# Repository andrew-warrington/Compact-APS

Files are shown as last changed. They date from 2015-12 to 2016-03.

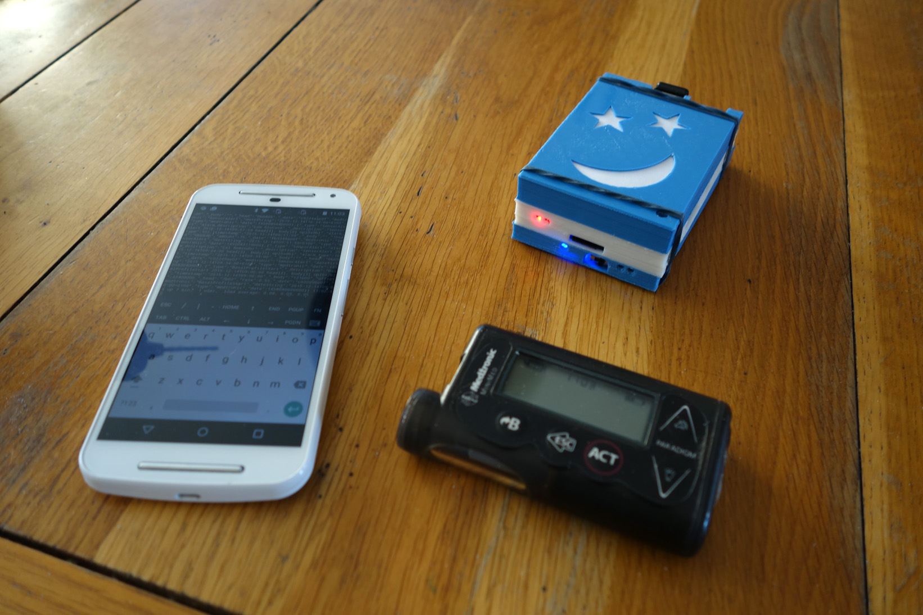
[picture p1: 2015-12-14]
Images/03 v1 assembled (except bolts) - angle 3.jpg

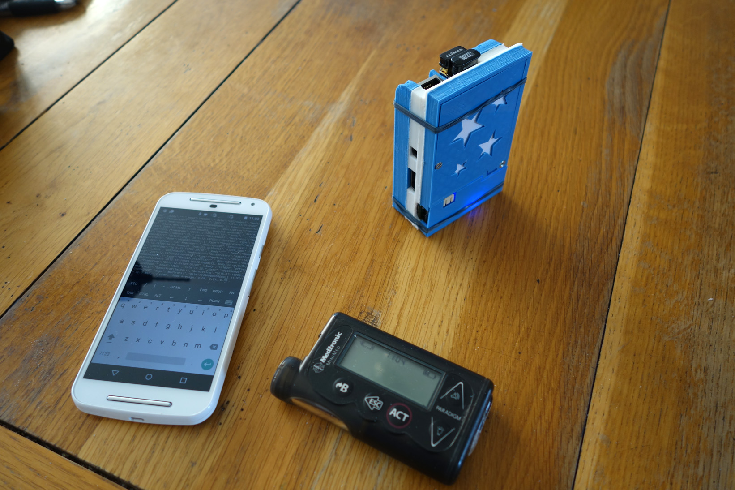
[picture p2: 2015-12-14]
Images/02 v1 assembled (except bolts) - angle 2.jpg

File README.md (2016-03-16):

# Compact-APS

This repository contains a compact hardware configuration for a DIY APS system based on the OpenAPS toolset. The goal of this build is to put everything needed for an OpenAPS-based implementation in a single box, including the battery. Pictures are available in the Images folder of this repository. The custom case files are in the Case folder.

- V1 is designed for a Raspberry Pi / Carelink config.
- V3.2 is designed for a Edison / TI USB CC1111 dongle config (mmeowlink)

If you are just starting out, I recommend the Edison v3.2 due to smaller size and longer battery life.

## V1 (Raspberry Pi) info

- Battery life 5 hours, with 5 hours recharge time while running.
- 10 cm long
- 6.2 cm wide
- 3 cm high

The device supports reading from Medtronic pumps & CGM, as well as Dexcom (I think! I don't have a Dexcom to test with...). It includes Wifi and BLE hardware support as well, via USB dongles.

The main tactic for reducing the footprint was to reverse one of the USB ports on the RPi2, so that the Carelink USB dongle is positioned over the RPi and not protrude outwards.

Due to the inclusion of an Adafruit PowerBoost charger, the device charges like a mobile phone - no need to shut it down and swap around USB cables. Just plug it in and it will charge while running. An attempt was made to include wireless charging as well - this was not immediately successful so will be added in a later version if possible.

The "Moon and stars" face on the top cover helps to remember how to place the device to have the optimum angle for communicating with the Carelink USB. If the face is looking at you, then it is likely in a good position for communication. :)

v1 design includes the following components:

- 1 Raspberry Pi 2 + SD card with NOOB Raspian and some extra space (standard stuff)
- 1 standard dual-port PCB-mountable USB connector (dismantled and rebuilt to face backwards - this would take some time to explain and so I will describe it further at a later time)
- 1 Carelink USB dongle
- 1 Adafruit PowerBoost 1000C
- 1 Power switch for the PowerBoost 1000C
- 1 Duracell DRSI9220 Lithium Ion battery (Samsung Galaxy Note replacement battery) - 2500 mAh
- 1 mobile phone battery connector (salvaged from an inexpensive Samsung mobile phone)
- 1 Wixel (to collect data from Dexcom CGM in an Xdrip configuration. Not tested as I don't have a Dexcom...)
- 1 Asus USB-BT400 Bluetooth 4.0 dongle (for Xdrip configuration but also might be used to connect via an app one day)
- 1 Edimax EW-7811UN Nano WiFi adapter
- 1 Medtronic remote control MMT-503EU, plus A23 12-volt battery, plus 3 x 4N25 optocouplers (this was for an experiment. it worked, but it was irritating, so it will be removed in v2)
- 1 home-designed and printed 3D case (files available in this repo)
- m2.5 x 8 nuts & bolts (cut down to various lengths as needed)
- m2.5 x 30 nuts & bolts (cut down to various lengths as needed)

+ bits of wire, solder, heat-shrink, the occasional piece of electrical tape, tools, sweat, tears.

Getting started? I started here, learning to desolder components on the Raspberry Pi.
https://blog.adafruit.com/2014/11/03/diet-raspberry-pi-its-only-wafer-thin-raspberry_pi-raspberrypi/

## V3.2 (Edison) info:
- Battery life 31+ hours, with 2.5 hours recharge time while running.
- 9.6 cm long
- 6.1 cm wide
- 2.8 cm high
... with rounded edges to be easier to put in a pocket!

v3.2 design includes the following components:
- 1 Intel Edison with mini-breakout board
    - includes WiFi and BLE on board
    - the Edison USB pins 4 & 5 are shorted to force it persistently into host mode
- 1 custom USB OTG adapter, made small to save space
- 1 power switch
- 2 Duracell DRSI9220 Lithium Ion battery (Samsung Galaxy Note replacement battery), in series for 7.4V
- 1 FatShark 7.4 LiIon battery, which was disassembled to yield:
    - The balance charging circuit
    - The balance charging cable
    - The power cable
- 1 FatShark 7.4v 1000mAh wall charger
- 1 TI USB dongle CC1111EMK868-915 running the excellent subg-rfspy and managed via mmeowlink
- 1 Medtronic remote controlled via Edison GPIO (which most people would not need)

The case was further simplified over v1 to not require any screws or bolts.... also because this helps reduce size! The top snaps on and off with clips.

I don't have time to document everything for this build at the moment unfortunately, but am happy to interact, answer individual questions, and improve the documentation from there based on what questions come up. Contact me if you want help.

Best wishes, Andrew Warrington

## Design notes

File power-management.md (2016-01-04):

Notes for an eventual document on power management

Ideas sourced from here, where original contributors are mentioned:
http://babaawesam.com/2014/01/24/power-saving-tips-for-raspberry-pi/

##Underclocking the RPi2. 

tested

Adding these lines to your config.txt (assuming RPi2 has not been overclocked)
* arm_freq_min=250
* core_freq_min=100
* sdram_freq_min=150

Do not add bullets before the lines. Reboot after adding the lines.

With these lines added, the processor runs at 250 mhz when idle, and returns to 900 mhz when active. I have seen no performance decrease from this change.

You can check your processor speed with the command

`cat /sys/devices/system/cpu/cpu0/cpufreq/scaling_cur_freq`

##Powering off USB & ethernet ports between loops (or permanently!)

tested

https://github.com/codazoda/hub-ctrl.c

worst case: returns to normal after a reboot

##Powering off HDMI

not yet tested

Warning, does not return to normal after a reboot. Recommend to add the HDMI power on command to crontab @reboot.

If your system is headless (no video output) you can turn off the HDMI port with:

`sudo /opt/vc/bin/tvservice -o`

to turn it back on:

`sudo /opt/vc/bin/tvservice -p`

This command will save you around 20-30mA.

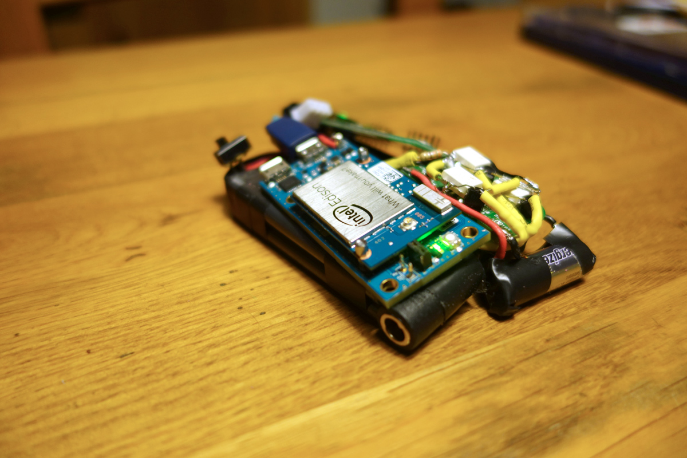
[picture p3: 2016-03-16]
Images/V3.2 interior showing at right the Medtronic remote and its batt, which most people dont need.JPG

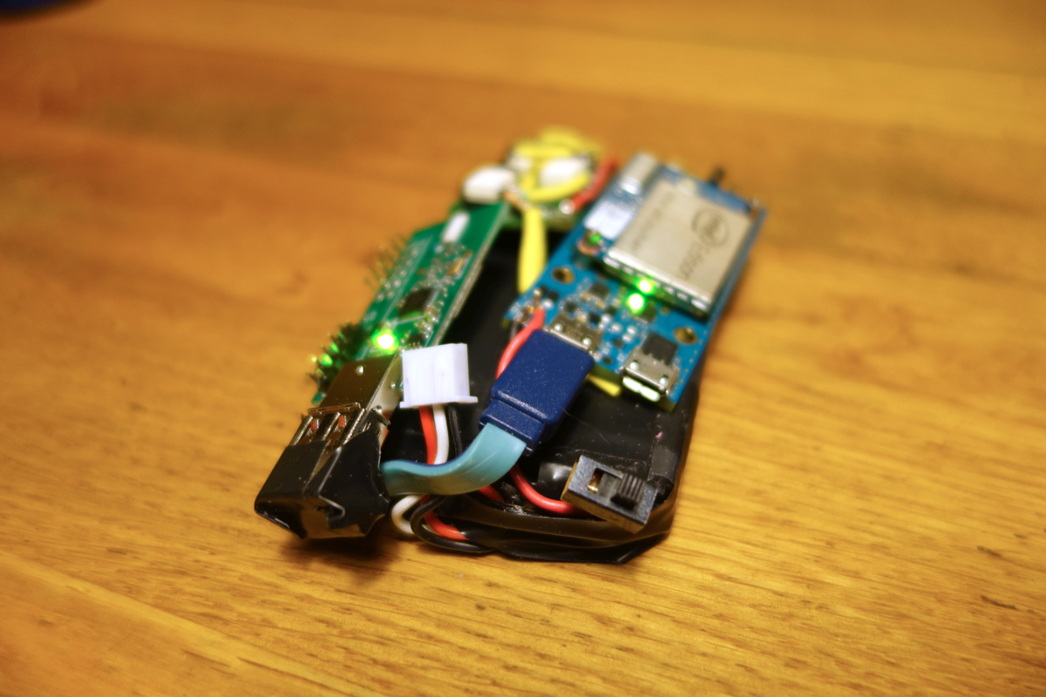
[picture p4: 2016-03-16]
Images/V3.2 interior showing custom USB connector, batt balancing cable and TI stick. Batts are underneath.JPG

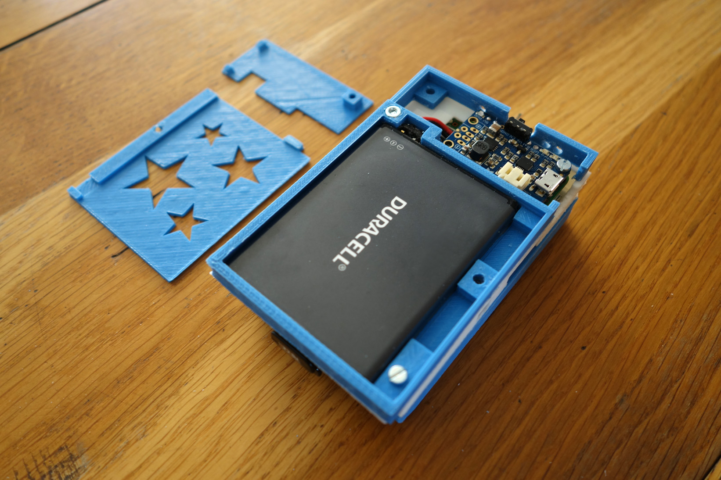
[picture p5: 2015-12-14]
Images/06 v1 underside showing the battery.jpg

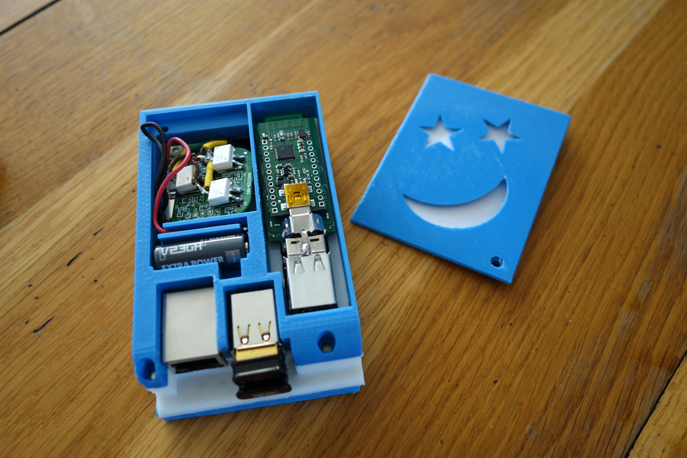
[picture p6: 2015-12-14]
Images/04 v1 under the lid.jpg

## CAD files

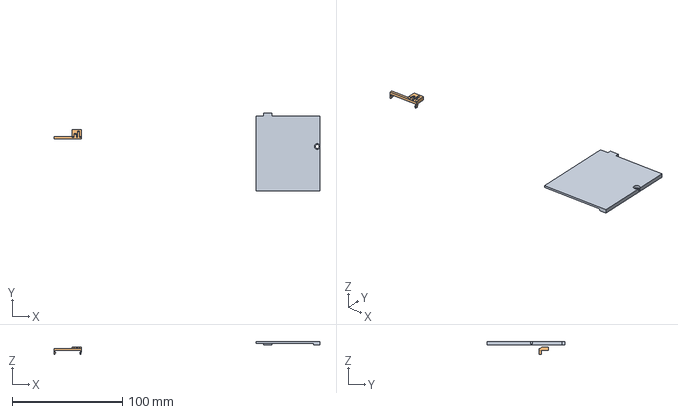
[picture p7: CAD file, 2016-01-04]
Case/FreeCAD/APS case v1.1.FCStd
241.8 x 71.0 x 11.5 mm
Main battery cover003

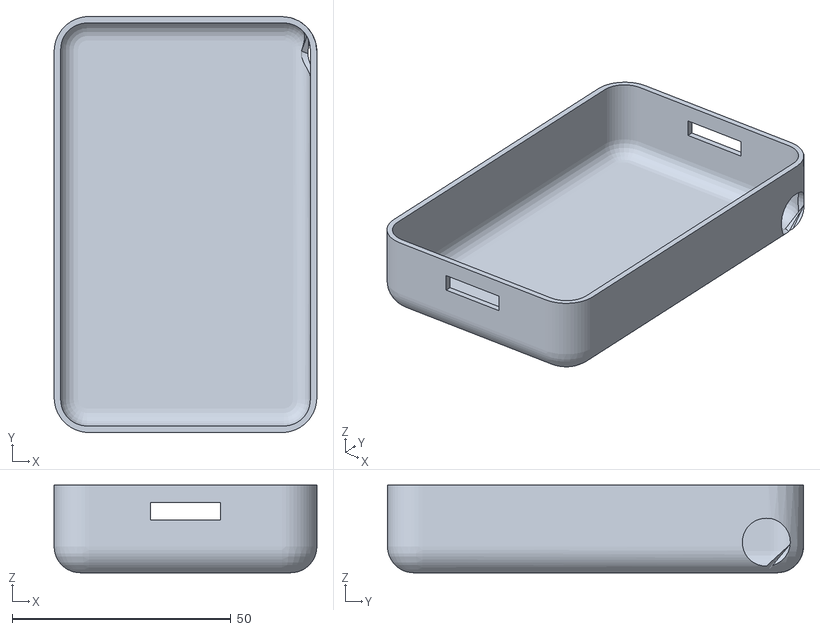
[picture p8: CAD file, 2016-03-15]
Case/STL mesh/CompactAPS v3.2 bottom final.stl
60.0 x 95.0 x 20.0

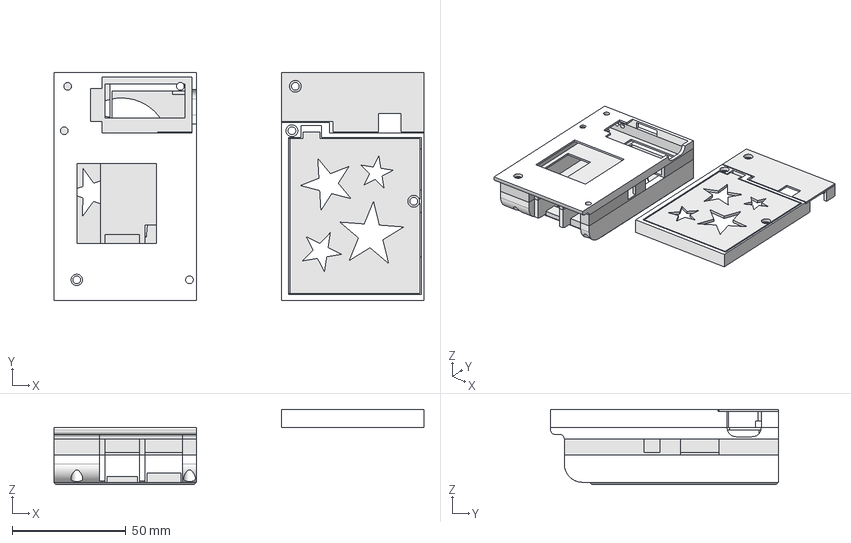
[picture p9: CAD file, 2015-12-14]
Case/FreeCAD/APS case v1.FCStd
162.5 x 100.0 x 33.0 mm
Pi case017
Pi case layer 3 009
Pi case layer 2 013
Main battery compartment022
Adafruit cover 004
Main battery cover010
Top cover 010

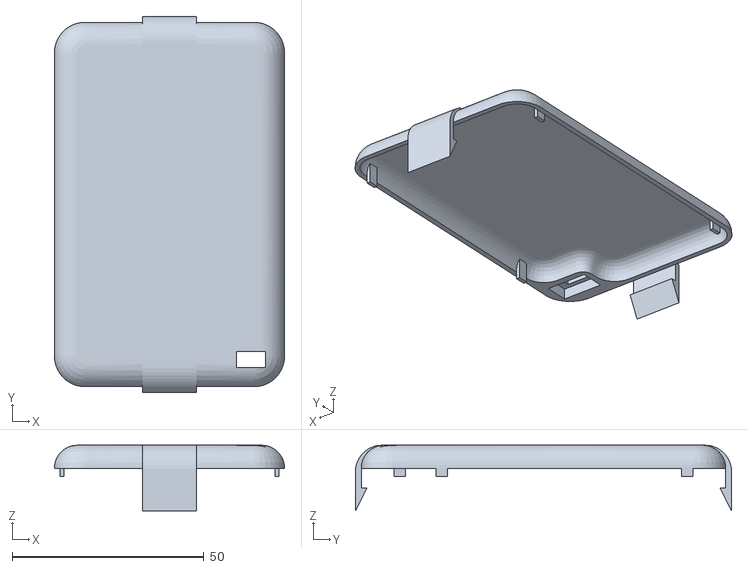
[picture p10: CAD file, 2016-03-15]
Case/STL mesh/CompactAPS v3.2 top final.stl
60.0 x 98.0 x 17.1

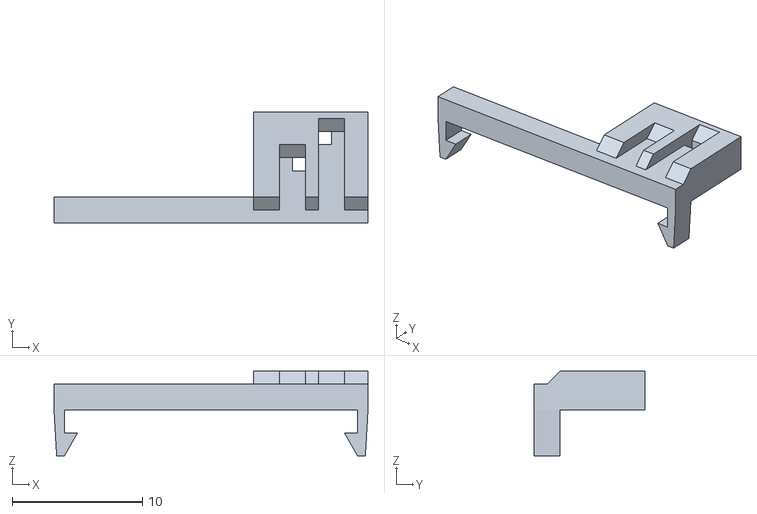
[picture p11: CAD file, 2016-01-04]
Case/STL mesh/v1 Carelink antenna connector.stl
24.1 x 8.50 x 6.50

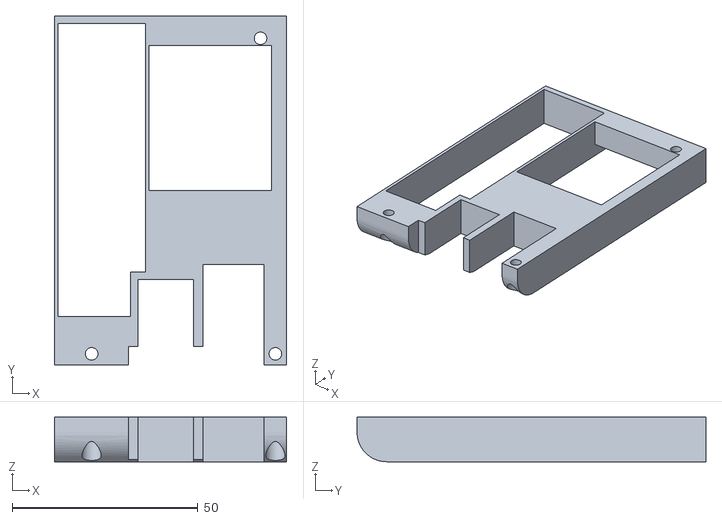
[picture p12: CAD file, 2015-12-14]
Case/STL mesh/v1 RPi housing layer 3.stl
62.5 x 94.0 x 12.0

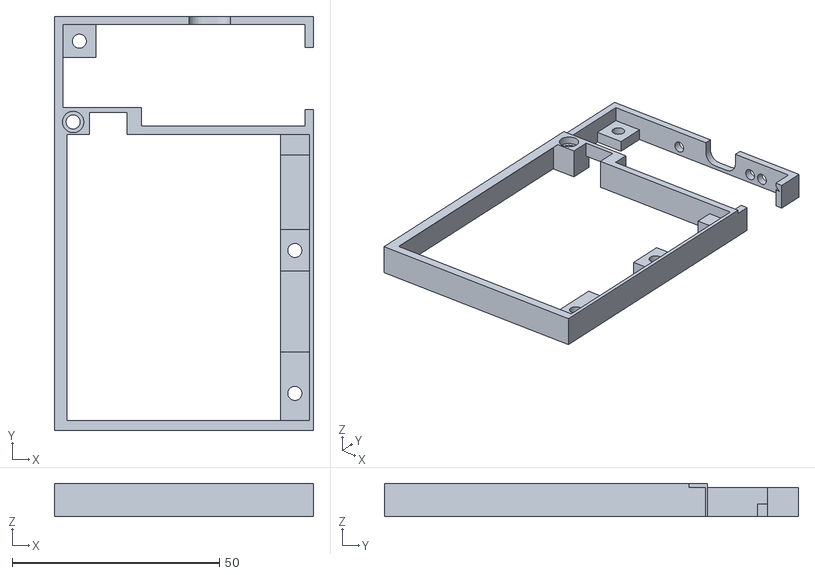
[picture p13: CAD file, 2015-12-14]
Case/STL mesh/v1 Battery compartment.stl
62.5 x 100.0 x 8.00

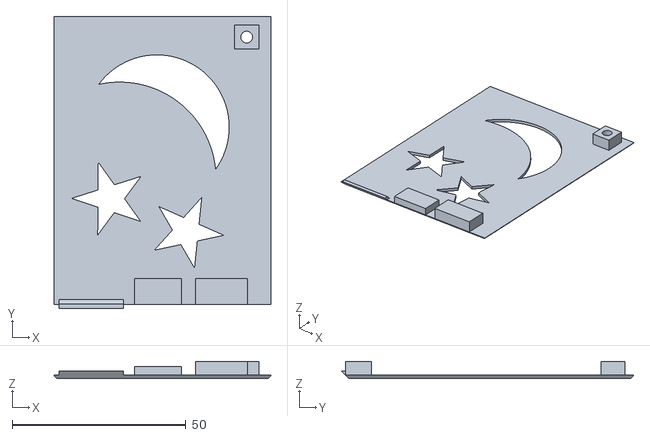
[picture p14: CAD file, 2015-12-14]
Case/STL mesh/v1 Top cover.stl
62.5 x 84.2 x 5.00

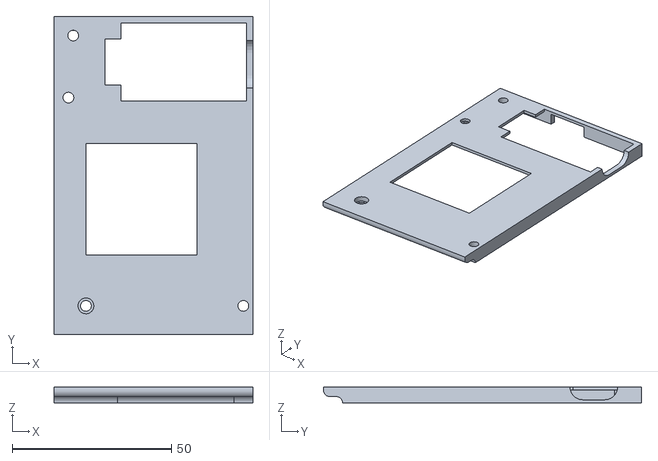
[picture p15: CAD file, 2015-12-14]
Case/STL mesh/v1 RPi housing layer 1.stl
62.5 x 100.0 x 5.00

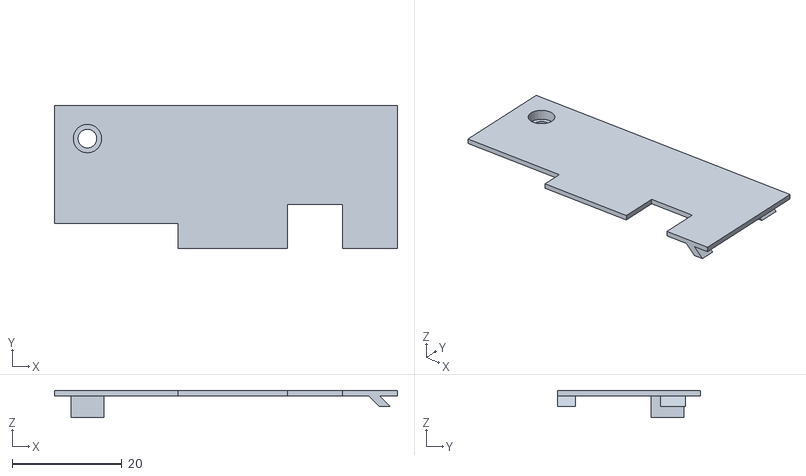
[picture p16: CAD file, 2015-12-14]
Case/STL mesh/v1 Powerboost cover.stl
62.5 x 26.0 x 5.00

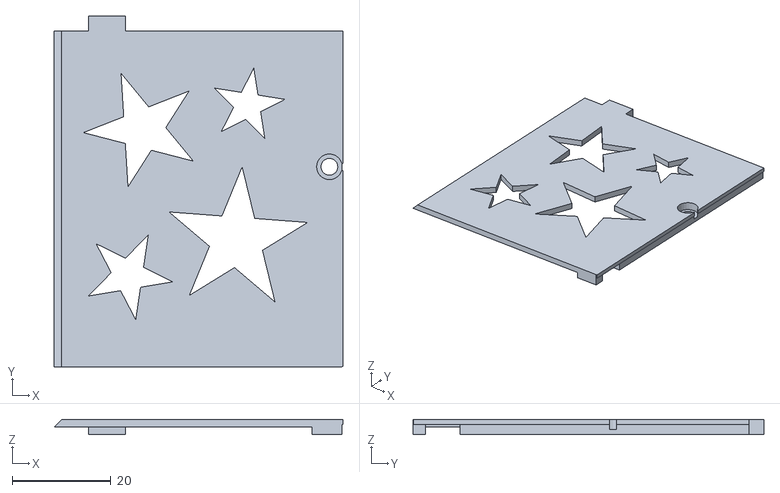
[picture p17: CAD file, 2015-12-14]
Case/STL mesh/v1 Battery compartment cover.stl
58.5 x 71.0 x 3.00

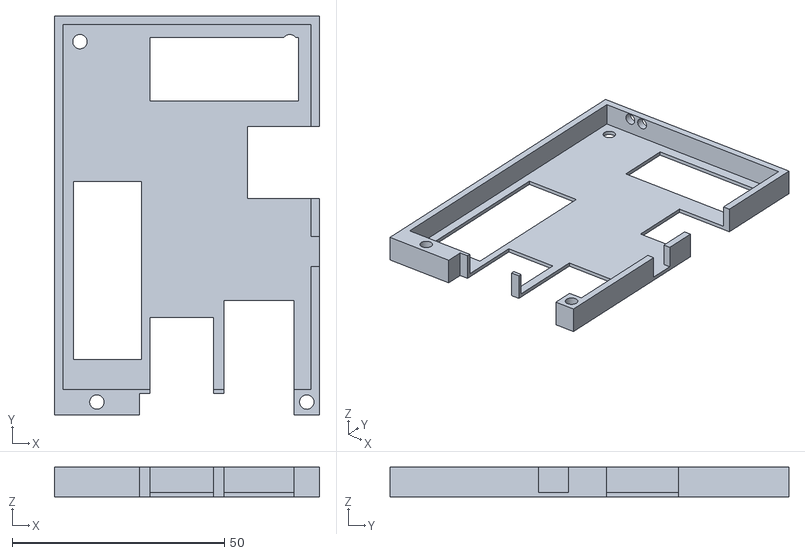
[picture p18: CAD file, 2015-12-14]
Case/STL mesh/v1 RPi housing layer 2.stl
62.5 x 94.0 x 7.00

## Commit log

2015-12-14 Initial
    Initial upload of images and 3D files
    [APS case v1.FCStd, v1 Battery compartment cover.stl, v1 Battery compartment.stl, v1 Powerboost cover.stl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]
2015-12-14 elastics will be removed when bolts are delivered. :)
2015-12-15 Carelink USB mystery solder pads
2016-03-15 Added v3.2 STL files
    [CompactAPS v3.2 bottom final.stl, CompactAPS v3.2 top final.stl]
